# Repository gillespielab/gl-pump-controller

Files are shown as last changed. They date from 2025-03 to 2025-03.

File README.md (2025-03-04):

# gl-pump-controller
This board is a SpikeGadgets ECU accessory, which acts as an RJ-45 breakout board for 8 or the DIO ports, and as a pump controller for the other 8 DIO ports in the bank. KiCAD is required to open/edit this project, and can be downloaded at https://www.kicad.org/download/

# Download Instructions
1. Clone the repo `git clone --recursive https://github.com/gillespielab/gl-pump-controller`
2. Open the KiCAD Symbol Editor. Then click: "File" -> "Add Library"
3. Select Global
4. In the prompt, select/open: gl-pump-controller/gl-electronics/symbols/Uploaded.kicad_sym

# BOM
Description | Component Number | Quantity | Part Number/Link
------------- | ------------- | ------------- | -------------
8-bit Buffer | U9-U10 | 2 | [SN74ABT541BPW](https://www.digikey.com/en/products/detail/texas-instruments/SN74ABT541BPW/1575499)
2x10 90deg Header Pins | J11 | 2 | [2057-PH2RA-20-UA-ND](https://www.digikey.com/en/products/detail/adam-tech/PH2RA-20-UA/9830622?s=N4IgTCBcDa4AwFYDsBaACgCTAJQIIrDhQFV8A5AERAF0BfIA)
8x1 RJ-45 Array | J9 | 1 | [432238182](https://www.digikey.com/en/products/detail/molex/0432238182/481095)
SSD Relays | U1-U8 | 8 | [AQY211EHAX](https://www.digikey.com/en/products/detail/panasonic-electric-works/AQY211EHAX/2804732)
1.02kO Resistor | R1-R8 | 8 | [RC1206FR-071K02L](https://www.digikey.com/en/products/detail/yageo/RC1206FR-071K02L/728390)
1uF Ceramic Capacitor | C1-C8 | 8 | [AGC1206X7R101-104KNE-CT](https://www.digikey.com/en/products/detail/venkel/AGC1206X7R101-104KNE-CT/21344624)
10kO Resistor | R9 | 1 | [ERJ-8ENF1002V](https://www.digikey.com/en/products/detail/panasonic-electronic-components/ERJ-8ENF1002V/89059?s=N4IgTCBcDaIAoEYAMA6JBpAYgYQCoFoA5AERAF0BfIA)
100uF Electrolytic Capacitor | C9 | 1 | [50ZLH100MEFC8X11.5](https://www.digikey.com/en/products/detail/rubycon/50ZLH100MEFC8X11-5/3563386)
2P2D Switch | S1 | 1 | [100DP1T2B4M6QE](https://www.digikey.com/en/products/detail/e-switch/100DP1T2B4M6QE/378873)
DC Power Jack | J10 | 1 | [163-179PH-EX](https://www.mouser.com/ProductDetail/Kobiconn/163-179PH-EX?qs=Xb8IjHhkxj5l2UOaIqcGCw%3D%3D)
JST PH-2 Connectors | J1-J8 | 8 | [Amazon](https://www.amazon.com/dp/B0C89MRNSH?ref=fed_asin_title&th=1)

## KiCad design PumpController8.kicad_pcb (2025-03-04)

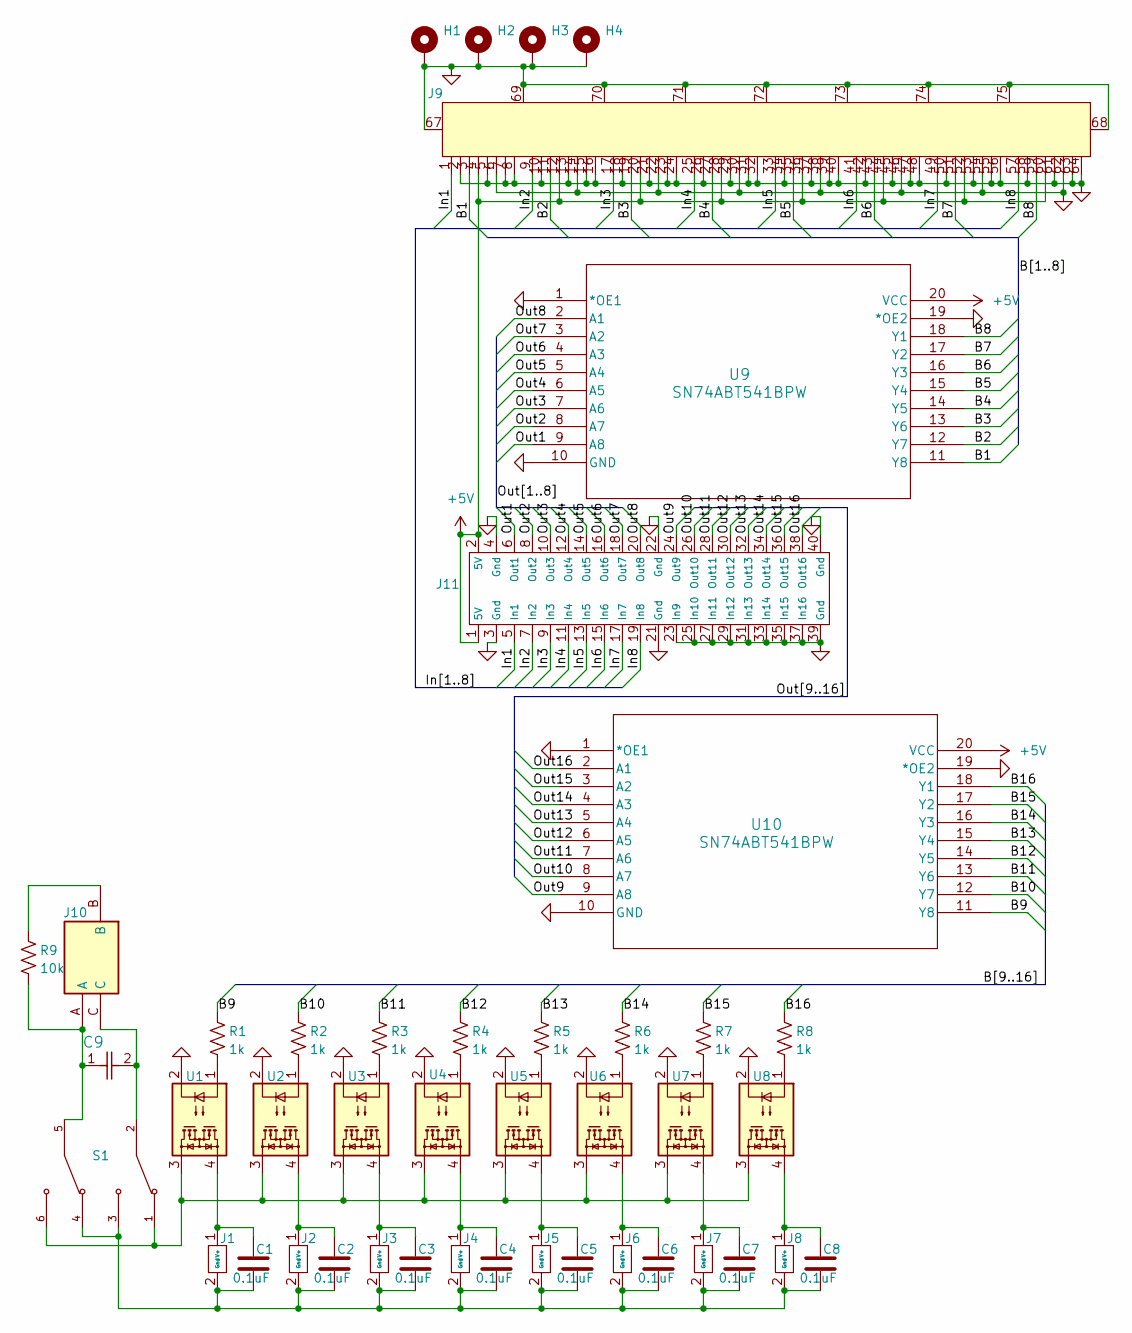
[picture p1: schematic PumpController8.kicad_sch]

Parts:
C1, C2, C3, C4, C5, C6, C7, C8: 0.1uF; C_1206_3216Metric_Pad1.33x1.80mm_HandSolder
C9: 50ZLH100MEFC8X11.5; CAP_YX_8X11P5_RUB
H1, H2, H3, H4: MountingHole_Pad; MountingHole_2.7mm_M2.5_ISO7380_Pad
J1, J2, J3, J4, J5, J6, J7, J8: JST-PH 2-Pin Socket; JST-PH 2-Pin Vertical
J9: CONN_43223-8182_MOL
J10: 163-179PH-EX; 163179PHEX; Mouser Part Number 163-179PH-EX
J11: ECU_Header_Pins
R1, R2, R3, R4, R5, R6, R7, R8: 1k; R_1206_3216Metric
R9: 10k; R_1206_3216Metric
S1: 100DP1T2B4M6QE; SW_100DP1T2B4M6QE; PARTREV G
U1, U2, U3, U4, U5, U6, U7, U8: AQY211EHAX
U9, U10: SN74ABT541BPW

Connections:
+5V: J9.4, J9.12, J9.20, J9.28, J9.36, J9.44, J9.52, J9.60, J11.1 (5V), J11.2 (5V), U9.20 (VCC), U10.20 (VCC)
/B1: J9.3, U9.11 (Y8)
/B2: J9.11, U9.12 (Y7)
/B3: J9.19, U9.13 (Y6)
/B4: J9.27, U9.14 (Y5)
/B5: J9.35, U9.15 (Y4)
/B6: J9.43, U9.16 (Y3)
/B7: J9.51, U9.17 (Y2)
/B8: J9.59, U9.18 (Y1)
/B9: R1.1, U10.11 (Y8)
/B10: R2.1, U10.12 (Y7)
/B11: R3.1, U10.13 (Y6)
/B12: R4.1, U10.14 (Y5)
/B13: R5.1, U10.15 (Y4)
/B14: R6.1, U10.16 (Y3)
/B15: R7.1, U10.17 (Y2)
/B16: R8.1, U10.18 (Y1)
/In1: J9.1, J11.5 (In1)
/In2: J9.9, J11.7 (In2)
/In3: J9.17, J11.9 (In3)
/In4: J9.25, J11.11 (In4)
/In5: J9.33, J11.13 (In5)
/In6: J9.41, J11.15 (In6)
/In7: J9.49, J11.17 (In7)
/In8: J9.57, J11.19 (In8)
/Out1: J11.6 (Out1), U9.9 (A8)
/Out2: J11.8 (Out2), U9.8 (A7)
/Out3: J11.10 (Out3), U9.7 (A6)
/Out4: J11.12 (Out4), U9.6 (A5)
/Out5: J11.14 (Out5), U9.5 (A4)
/Out6: J11.16 (Out6), U9.4 (A3)
/Out7: J11.18 (Out7), U9.3 (A2)
/Out8: J11.20 (Out8), U9.2 (A1)
/Out9: J11.24 (Out9), U10.9 (A8)
/Out10: J11.26 (Out10), U10.8 (A7)
/Out11: J11.28 (Out11), U10.7 (A6)
/Out12: J11.30 (Out12), U10.6 (A5)
/Out13: J11.32 (Out13), U10.5 (A4)
/Out14: J11.34 (Out14), U10.4 (A3)
/Out15: J11.36 (Out15), U10.3 (A2)
/Out16: J11.38 (Out16), U10.2 (A1)
GNDS: H1.1, H2.1, H3.1, H4.1, J9.2, J9.5, J9.6, J9.7, J9.8, J9.10, J9.13, J9.14, J9.15, J9.16, J9.18, J9.21, J9.22, J9.23, J9.24, J9.26, J9.29, J9.30, J9.31, J9.32, J9.34, J9.37, J9.38, J9.39, J9.40, J9.42, J9.45, J9.46, J9.47, J9.48, J9.50, J9.53, J9.54, J9.55, J9.56, J9.58, J9.61, J9.62, J9.63, J9.64, J9.67, J9.68, J9.69, J9.70, J9.71, J9.72, J9.73, J9.74, J9.75, J11.3 (Gnd), J11.4 (Gnd), J11.21 (Gnd), J11.22 (Gnd), J11.23 (In9), J11.25 (In10), J11.27 (In11), J11.29 (In12), J11.31 (In13), J11.33 (In14), J11.35 (In15), J11.37 (In16), J11.39 (Gnd), J11.40 (Gnd), U1.2, U2.2, U3.2, U4.2, U5.2, U6.2, U7.2, U8.2, U9.1 (*OE1), U9.10 (GND), U9.19 (*OE2), U10.1 (*OE1), U10.10 (GND), U10.19 (*OE2)
unnamed: C9.1, J10.A, R9.2, S1.5
unnamed: C9.2, J10.C, S1.2
unnamed: C1.2, C2.2, C3.2, C4.2, C5.2, C6.2, C7.2, C8.2, J1.2 (Gnd), J2.2 (Gnd), J3.2 (Gnd), J4.2 (Gnd), J5.2 (Gnd), J6.2 (Gnd), J7.2 (Gnd), J8.2 (Gnd), S1.3, S1.4
unnamed: C1.1, J1.1 (V+), U1.4
unnamed: C2.1, J2.1 (V+), U2.4
unnamed: C3.1, J3.1 (V+), U3.4
unnamed: C4.1, J4.1 (V+), U4.4
unnamed: C5.1, J5.1 (V+), U5.4
unnamed: C6.1, J6.1 (V+), U6.4
unnamed: C7.1, J7.1 (V+), U7.4
unnamed: C8.1, J8.1 (V+), U8.4
unnamed: J10.B, R9.1
unnamed: R1.2, U1.1
unnamed: R2.2, U2.1
unnamed: R3.2, U3.1
unnamed: R4.2, U4.1
unnamed: R5.2, U5.1
unnamed: R6.2, U6.1
unnamed: R7.2, U7.1
unnamed: R8.2, U8.1
unnamed: S1.1, S1.6, U1.3, U2.3, U3.3, U4.3, U5.3, U6.3, U7.3, U8.3

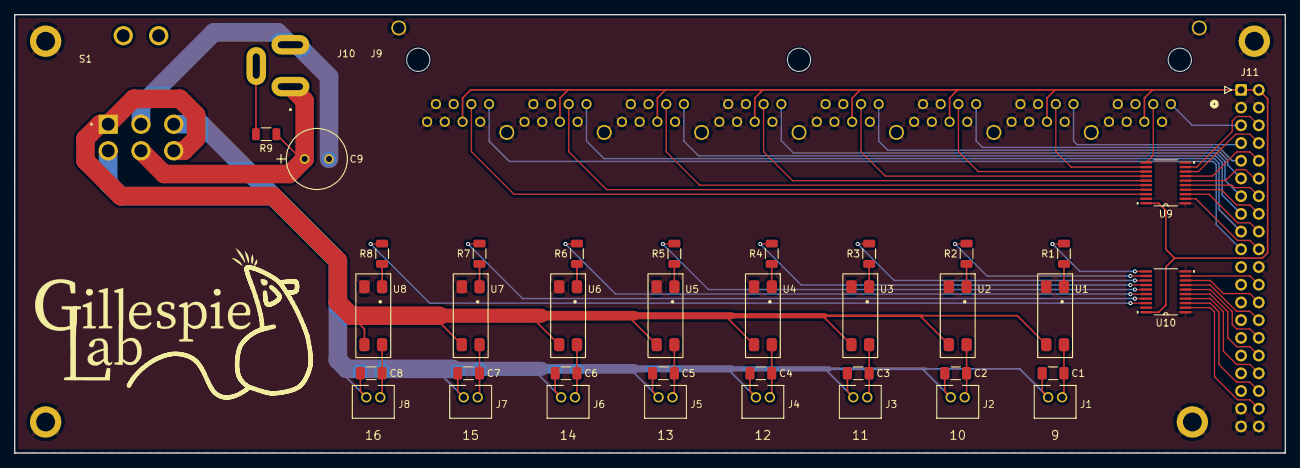
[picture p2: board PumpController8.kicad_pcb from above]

Board: 2 copper layers, 182.2 x 62.9 mm, 44 parts (0 on the bottom side), 63 nets.
